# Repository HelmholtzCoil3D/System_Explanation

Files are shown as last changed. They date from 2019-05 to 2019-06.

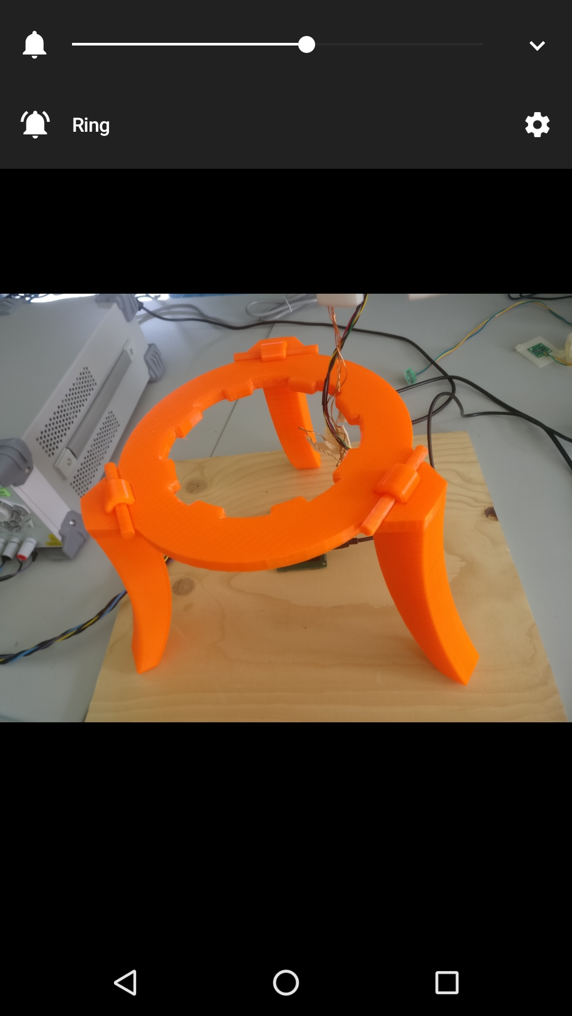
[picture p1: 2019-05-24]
Images/Print results/Screenshot_20190524-094820.jpg

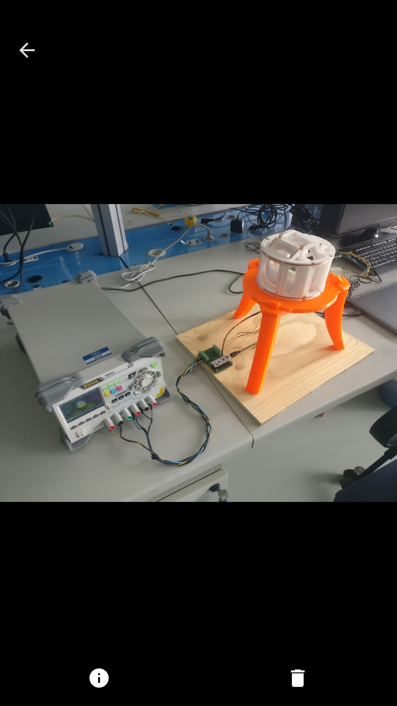
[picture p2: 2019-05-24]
Images/Final Results/Screenshot_20190524-155419.jpg

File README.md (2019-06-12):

# 3D Helmholtz coil system

This document explains how the system was made and how it works, with the purpose to make the reproduction of the project possible.

- [3D Helmholtz coil system](#3d-helmholtz-coil-system)
- [Objective of the project](#objective-of-the-project)
- [Base Knowledge](#base-knowledge)
- [Blocks diagram](#blocks-diagram)
- [Helmholtz coils design](#helmholtz-coils-design)
  - [Simulator](#simulator)
    - [Input parameters:](#input-parameters)
    - [Console results](#console-results)
    - [Graphical Results](#graphical-results)
    - [Simulator results](#simulator-results)
  - [3D models](#3d-models)
    - [3 axis helmholtz coil 3D model](#3-axis-helmholtz-coil-3d-model)
    - [Sensor and sample support 3D model](#sensor-and-sample-support-3d-model)
    - [Pegs 3D model](#pegs-3d-model)
    - [3 feet support 3D model](#3-feet-support-3d-model)
  - [3D Print results](#3d-print-results)
    - [Coils support print](#coils-support-print)
    - [Sensor/Sample support](#sensorsample-support)
    - [Pegs](#pegs)
  - [3 Feet support](#3-feet-support)
  - [Coils winding](#coils-winding)
  - [Practical results](#practical-results)
    - [Inner coil](#inner-coil)
    - [Middle coil](#middle-coil)
    - [External coil](#external-coil)
    - [Data analysis](#data-analysis)
- [Magnetic sensor](#magnetic-sensor)
- [Controller](#controller)
  - [Power Supply](#power-supply)
  - [H-bridges](#h-bridges)
  - [MCU](#mcu)
  - [New system Block Diagram](#new-system-block-diagram)
- [Integration](#integration)
  - [system_current_finder.py and system_measurement_procedure.py](#systemcurrentfinderpy-and-systemmeasurementprocedurepy)
  - [system_plot.py](#systemplotpy)
  - [system_realtime_field_adjusting.py](#systemrealtimefieldadjustingpy)
  - [System validation](#system-validation)
- [PCBs](#pcbs)
  - [Sensor PCB](#sensor-pcb)
  - [System PCB](#system-pcb)
- [Final result](#final-result)
- [System applications](#system-applications)

# Objective of the project

This project aim is to prototype some kind of system control it automaticaly and make some fields setups in static applications.

The idea behind this project is to create a homogeneous field in some defined region where magnetic samples can be tested with a totaly known field

<p align="center">
  
  
</p>

<p align="center">
  
</p>

The desired features in this case would be a region with errors bellow 1%, the maximium difference of the magnetic field strenght in two different points and angles with less than 1° of difference between two different points of the homogeneous region. A magnetic flux density range of 1 uT to 1 mT is desired in this region.

The region defined for the prototype at first is a **20 mm³**  region

**The system itself just generate the field**, the magnetic sample must have its own system to generate the data for posterior analysis. Analisys can be made based in the known direction and amplitude of the homogeneous region magnetic field.

# Base Knowledge

To create a homogeneous field in some free space region, the concept used was the [Helmholtz coil] that can create a homogeneous field inward from the coils to the geometric center of the estructure, the more in the center, the more homogeneous the field is.

Exitating the coils with a known current generates a known [magnetic field] (H) that is related to the magnetic flux density (B) by the permeability ($\mu$) of the material, in this case the air ([1.00000037])

The B can [saturate] depending on the material, in this case it will not happen so there are no linearity problems

Knowing that the magnetic field will be linear, so a 3 axis Helmholtz coil can be design to generate the arbitrary homogeneous magnetic field, remembering that this system must compensate the [earth magnetic field]

#  Blocks diagram

The system blocks diagram can be represented as follows:
<p align="center">
  
</p>

The main parts of the system:
-   Helmholtz coils to generate the field
-   Controller to control the generated field throught magnetic sensors readings and current supply for the coils
-   Interface to give properly the user commands to the controller

# Helmholtz coils design

## Simulator

To design the needed helmholtz coils, an open source python library was used, [magpylib], this library is capable to calculate magnetic field, through analytical solutions, of permanent magnets and current lines or current loops.

In fact the application is static, so the helmholtz can projected as current loops placed in a helmholtz coil shape.

<p align="center">
  
</p>

 From the cross-cut section the parameters for the coils calculation can be extracted as the following figure:

<p align="center">
  
</p>

The details about the calculator can be seen in the [Helmholtz coil calculator] and [Auxiliar library] files. Giving some parameters to the calculator, it gives us the necessary coil diameter to achieve the desired field in the center of the coil and graphics that shows the field strenght in the 3 vectors of the field separeted (x,y,z) and from this an analysis can be made to determine the homogenity of the field generated by each coil, amplitude and angle error relative to the center in the desired homogeneous region. Following the input and the results in this project.

### Input parameters:

Those are the input parameters for the calculator to find the diameter necessary the design each coil, following previous figure standards.

``` python
# have to use a little bit bigger value than wireExternalDiameter, if not, the wire will not fit inside
AllCoilsWireDiameter = (0.56 + 0.047)*1.09   # Wire diameter in mm (from dataSheet)

minRes = 0.06736                            # Ohms/m (from dataSheet)
nominal = 0.06940                           # Ohms/m (from dataSheet)
maxRes = 0.07153                            # Ohms/m (from dataSheet)

wireResistence = maxRes                     # Ohms/m (from dataSheet)

# z First Coil configuration

zInitialValueCoilDiameter = 80 # Initial value for the function that calculates the precise diameter

zCoilCurrent = 0.5             # Amperes
zLoopsInEachEvenLayer = 10     # The number of loops in each layer
zEvenLayers = 7                # The evenlayers always have to be equal to oddLayers or oddLayers + 1
zOddLayers = 7
zDesiredField = 1.25           # The desired field in the center of the Helmholtz coil

# y Second Coil configuration

yCoilCurrent = 0.5             # Amperes
yLoopsInEachEvenLayer = 6      # The number of loops in each layer
yEvenLayers = 3                # The evenlayers always have to be oddLayers + 1 or equal oddLayers
yOddLayers = 3
yDesiredField = 0.25           # The desired field in the center of the Helmholtz coil

# x Third Coil configuration

xCoilCurrent = 0.5             # Amperes
xLoopsInEachEvenLayer = 7      # The number of loops in each layer
xEvenLayers = 3                # The evenlayers always have to be oddLayers + 1 or equal oddLayers
xOddLayers = 3
xDesiredField = 0.25           # The desired field in the center of the Helmholtz coil
```

### Console results

Those are the results that shows up in the standard output, in this case the console of spyder, those results can estimate how much wire in meters and the power in watts that will be dissipated on each helmholtz coil individualy.



### Graphical Results

Those are the graphical results of the calculator. For each coil a graphic is generated with the amplitude of the magnetic field of a slice in the center of the coil, this slice must have the region of interest, it also displays a 3D graphic of what the system looks like. Those graphics can help to estimate the homogenity level of the whole region.

<p align="center">
  
  
</p>

<p align="center">
  
  
</p>

<p align="center">
  
  
</p>

As can be seen in the next figures, the calculator estimates the interference of the cables used to bring the current to the coils, the current passing throught them generates a field and it can be compared with the field generated for each coil. Just the field of the connectors is showed in the graphics. Another that can be seen is if the coils will be inside each other in the 3D representation, it's shown in the 3 coils figure that the coils don't touch each other in this case.

<p align="center">
  
  
</p>

<p align="center">
  
  
  
</p>

### Simulator results

After checking all the homogenity and interference stuff, the interested parameters to construct the coils support are shown in the next table:

Wire External Diameter = 0.6 mm

|Coils| Radius | Coil Width| Coil Height|
|:-:|-|-|-|
| Inner | 42.5 mm | 6.6 mm | 9.65 mm |
| Middle | 56.15 mm | 4 mm | 5.5 mm |
| External | 66.5 mm | 4.65 mm | 5.5 mm |
**\* rouded values**

## 3D models

With the high precision of the 3D printers ($\pm$ 1 $\mu$m) the idea was doing the 3 helmholtz coils all together in the same mechanical part, 1 piece. With this, the misalignment problems would desappear.

Misalignment example:
<p align="center">
  
</p>

To design the 3D model the utilized software was [solidWorks], a comercial software for 3D models design, good for geometric models. The design was made based in the simulating results. Besides the coils, the sensor and sample placement should be designed together with the coil, to make it easier to think the supports was separated and connected throught holes and pegs.

### 3 axis helmholtz coil 3D model

The 3 axis helmholtz coil 3D model design can be seen in the following images:

<p align="center">
  
  
  
</p>

It has some holes inside to attach the sensor support and a bigger hole in the middle for the cables to link the sensor to the system. In the bottom some support points to make the coil stable in the table.

### Sensor and sample support 3D model

After some tests, the model achieved for the PCB support is shown in the following image:

<p align="center">
  
  
</p>

This model perfectly fits inside the coils support model, using the internal part to support the sensor of the system and the more external pegs and holes to support the sample. Notice that the external support is designed in such a way that the sample stays in the middle of the coils. If the sample change, the user can design another 3D model for the support to adapt the coil usage to an especific application

### Pegs 3D model

To attach the PCB support to the coils support some pegs was designed with diferent diameters, using the fact that the printer has more precision than $\pm$1 $\mu$m:

<p align="center">
  
  
</p>

Using 50 $\mu$m of difference between the pegs, will make it safe to fit in the previous models holes, testing which diameter is beter to use.

### 3 feet support 3D model

To avoid some induction fields problems that could appear for some kind of measurements, a 3 feet support for the coils support was design that the coils support just fits inside of the 3 feet support and make some distance between the table metal supports and the coils.

<p align="center">
  
  
  
</p>

## 3D Print results

The company have its own 3D printers, one with really high resolutions for tiny parts and another with less resolution but with more space to print. The material is not so rigid in the high resolution printer and the prints have problems in the pos-printing process that causes some bendding problems, so for the coils support the print was made by [Reprap] Austria, that was more cheap and perfect printed than with the company printer. For the other models, the company printer was enought to do the job.

The Reprap Austria 3D printer size limit is **32**x**36**x**42** **cm**, been the largest coil external diameter around 15 cm, the printing size is fairly ok and if the company needs a bigger coil with different especification, it can be printed.

### Coils support print

The Coils support was ordered and the result can be seen:
<details>
<summary> <b>Click here to see the Coil support print result</b> </summary>
<p align="center">
  
</p>

**There's a sensor support inside of the coils printed with the company printer, that fitted really nice inside**
</details>

### Sensor/Sample support

Printed in the CTR high resolution printer:

<p align="center">
  
  
</p>

<p align="center">
  
  
</p>

### Pegs

Printed in the CTR high resolution printer:

<p align="center">
  
</p>

## 3 Feet support

Following figure shows the 3 feet suppport printed in the lower resolution printer, that is also very good and it's used for bigger 3D models.

<p align="center">
  
</p>

## Coils winding

After doing the windings really carefull, maintaining the [wire] stretched while doing each turn, it helped to get the wire really fit in the coils support. The arrangement to stretch the wire can be seen in the next image, its an improvised tool that makes some pressure in the reel, extremely important to make the coils the most near to the simulation position of the wires.

<p align="center">
  
  
</p>

 The [hot glue] was used to mantain the cables fixed in the coils suppor, the result of the 3 axis coil can be seen in the following image:

<p align="center">
  
  
</p>

Each of the six coils was done individualy, doing the inside coils first, and then connected with a solder point with the respective pair (2 coils in X direction to form the X helmholtz coil for example)

## Practical results

To validate the python calculator, some measurements was made, like the resistence, inductance and generated field for each coil. Each coil is named now by inner, middle and external coil. The measurements are discussed subsequently.

### Inner coil

This coil is the most inside coil (inner), it has the most intense field of the 3 coils, that's why it's the inside coil and the one that have more windings.

Coil teorethical features:
|Feature| Value |
|-|-|
|Current| 0 ~ 0.5 *A*|
|Magnetic field generated| 0 ~ 1.25 *mT* |
|MagField/Current ration| 2.5 |
|Coil resistence| 5.264 $\Omega$|

Mesured resistence ($\Omega$), inductance (mH):

<p align="center">
  
  
</p>

The mesured field with the 500 mA (powersupply and sensor image):

<p align="center">
  
  
</p>

### Middle coil

The middle coil is the one in between other 2 coils and its purpose is to cancel the earth magnetic field.

Coil teorethical features:
|Feature| Value |
|-|-|
|Current| 0 ~ 0.5 *A*|
|Magnetic field generated| 0 ~ 0.25 *mT* |
|MagField/Current ration| 0.5 |
|Coil resistence| 1.689 $\Omega$|

Mesured resistence, inductance:

<p align="center">
  
  
</p>

The mesured field with the 500 mA (powersupply and sensor image):

<p align="center">
  
  
</p>

### External coil

External coil is the name of the further coil from the center, the biggest, same purpose as middle coil.

Coil teorethical features:
|Feature| Value |
|-|-|
|Current| 0 ~ 0.5 *A*|
|Magnetic field generated| 0 ~ 0.25 *mT* |
|MagField/Current ration| 0.5 |
|Coil resistence| 2.356 $\Omega$|

Mesured resistence, inductance:

<p align="center">
  
  
</p>

The mesured field with the 500 mA (powersupply and sensor image):

<p align="center">
  
  
</p>

### Data analysis

In the previous images can be seen the current to excitate the coils and the magnetic field read from the sensor in **$\mu$T** (The sensor will be explained in the next topic), the magnetic field is already a mean of 30 measurements. The sensor can not be positioned perfectly aligned with the coils directions, then the norm of the difference should be taken to express the real value of the field generated by the coils. 

A python script ([Coil Features]) was made to handle those simple calculations and the results are shown in the next image.



As seen, the field error is really tiny (bellow 2%), maybe because the windings somehow are no perfectly round and it can be reflected in this tiny error.

In the resistance the error was quite big, but for an estimative could be helpfull to have some power dissipation notion.

# Magnetic sensor

The magnetic sensor is a really important part of the project, because it will provide the measurements to understand if the coils are working properly or not and the closes some loop to adjust the field if necessary. Some research was done and some sensors was tried. The first solution encounted was the [LIS3MDL] sensor, it's for compass application and had a good range of measurement for the application, but with some tests it showed really bad response to offset errors, so another one was tried, an upgraded version of this sensor from the same company ([ST]), [LSM303D], but somehow there was the same problems. Then researched for another companies that would be specialized in magnetic sensors and then found [MEMSIC], and searching for magnetic sensors, found one that fitted in the application, [MMC3416].

The sensor have I²C interface, also have a really interesting measurement procedure, where the [set/reset] operation can be applied to extract a better measurement, the downside of this procedure is that it takes time. In this project is not a problem because the application is static.



A usefull thing to do is buy the evaluation board in this case, that have everything in hardware set up to just use the sensor. To project, order and solder the PCB takes time, so to develop it faster the [MMC3416 evaluation board] was used.



# Controller

The controller part of the blocks diagram could be anything that could:

-   Control the coils field
-   Read the sensor measurements
-   Interpret the user commands

For those tasks more especificaly was needed something that could have some: 
-   I²C comunication (sensor) 
-   Current source adjustable with a good resolution, to achieve the field resolution bellow 1 uT
-   A way to change the current polarity in the coils
-   Kind of USB communication to stablish comunication with the computer (where the user interface would be implemented)

It's difficult to have all those tasks already integrated so some research was done to what to use.

## Power Supply

In one way or another, a power supply must be used to provide the energy for the coils, can be as a voltage source or a current source. Operating in the voltage source mode would imply some external controller to adjust the right current for the coils, in other way with the current source mode, the power supply must have some kind of electronic current control integrated to use this in the system. After some research found [Rigol DP800] series, specifically the 831A model, that have 0.1 mA resolution of current control with 3 channels and can be controlled by software, perfect for this application.

The software control can be done through the [python visa] that are some special libraries used to control mesurement equipaments.

[python visa]:https://pyvisa.readthedocs.io/en/latest/

<p align="center">
  
</p>

## H-bridges

To control the current polarity in the coils, a classical but really good solution can be used, the [H-bridge] control.

    

It's system composed by 2 switches, as shown in the first figure of this section. The circuit have 3 possible states, that are shown in the figures, one state is everything open (turn off), and the other two is the current flowing to one direction of the load and the other the current is flowing in the another direction.

A lot of research was done, and most of the integrated H bridges have underload protection what is not desirable for this project, but one was found with the potential to be used, the [DRV8838DSGR] IC.



This IC works with 2 digital pins to control the states and is based on N-Mosfets. It can operate in 0~11 V range which fit the application. The only downside is the fact that the load supply is not isolated from the control supply.

The power supply choosed for the current control has one of its channels a negative voltage source that is internaly connected to another positive channel. In this case the [DRV8838DSGR] H-bridge the internal connection in the references of the supply for the logic (Vcc) and the supply for the load (VM) would cause a short circuit between the negative voltage and the reference in the power supply.

For this specific channel, a different solution to also isolate the channel must be implemented. After some research the best solution would be use 4 relays to do the switch role controlling it in such a way to stay in the 3 possible states of the H-bridge. The component choosed for the switch was [CPC1002N], it's a solid-state relay, basicaly an optocoupler with more current capacity than a normal optocoupler.



## MCU

To control the H-bridges and the sensor a microcontroller can be used. The microcontroller must have:
-   I²C interface peripherical
-   At least 6 free digital pins (H bridges)
-   USB comunication peripherical

And for this the [STM32L4] was choosed because of the versatility, powerful processing, easy usage and low cost, And it has all the features necessary for the system.

[STM32L4]:https://www.st.com/resource/en/datasheet/stm32l432kc.pdf

To program this controller the [stm32CUBE] was used to generate the base code and the [atollic] to edit, compile, debug and program the code.

The main code developed for the microcontroller is in those files:

-   [main.c]
-   [main.h]
-   [lib_aux.c]
-   [lib_aux.h]
-   [MCC3416_def.h]

To have more robustness the system was developed in a [finite state machine] shape, with one state for each operation.

When the microcontroller starts-up the first thing that it does is asking throught USB comunication, the size of the mean for each measurement and the time (ms) to do it, of course the bigger the measurements number, bigger the overhead will be.

After the 2 responses, the system start to operate in the state machine where there are 9 possible states besides Iddle:

|State symbol| Description of the state|
|:-:|:-|
|'D'| Procedure mean size of measurements and return the mean in the USB comunication getting back to iddle after|
|'I'| Sets the polarity to 'set' in the H-bridge connected to the channel 2 and sends back "'I' done!"|
|'i'| Sets the polarity to 'reset' in the H-bridge connected to the channel 2 and sends back "'i' done!"|
|'M'| Sets the polarity to 'set' in the H-bridge connected to the channel 3 and sends back "'M' done!"|
|'m'| Sets the polarity to 'reset' in the H-bridge connected to the channel 3 and sends back "'m' done!"|
|'E'| Sets the polarity to 'set' in the H-bridge connected to the channel 1  and sends back "'E' done!"|
|'e'| Sets the polarity to 'reset' in the H-bridge connected to the channel 1 and sends back "'e' done!"|
|'S'| Set all the polarities to a reference and sends back "'S' done!"|
|'C'| Perform continuos measurement procedures and send then to the USB comunication without getting back to the IDDLE state|

<p align="center">
  
</p>

The 'I', 'i', 'E' and 'e' states control just the digital pin for the [DRV8838DSGR] H-bridge, the 'M' and 'm' states control 4 digital pins to control the H-bridge formed by the relays [CPC1002N].

After a state sending, the system response with a '"state" done!' for debug and flow control. The exception on this is the 'D' and 'C' states that respond with the data directly.

The USB comunication is based on UART, the baud rate of the comunication is 256000 bauds

## New system Block Diagram

With the definition of how the control will be done and with what, The blocks diagram can be redrawed into the following image:

<p align="center">
  
</p>

# Integration

With a research about how to integrate the VISA application and the USB data from microcontroller, the conclusion was to use python libraries to get the information from USB and to control the power supply, using a structered diferent scripts to do some procedure with this.

The main python libraries used for USB communication:
-   [pyvisa]
-   [pyserial]

for some data processing and to show graphics:
-   [numpy]
-   [matplotlib]

and used some standard libraries as:
-   [time]
-   [csv]
-   [re]

The existing scripts until now following:
-   [auxLib.py]
-   [system_current_finder.py]
-   [system_measurement_procedure.py]
-   [system_realtime_field_adjusting.py]
-   [spinning_Compass.py]
-   [system_plot.py]

auxLib is the library with the <s>Black Magic</s> functions that do all the work on the others scripts.

## system_current_finder.py and system_measurement_procedure.py

It calculates the necessary current to have a range of field from 'lowerFieldLimit' to 'upperFieldLimit' field, with a step of 'fieldResolution'. Running the system current finder script gives a `csv` file that contains the information to later apply it with the system measurement procedure file.

Something important to **take care** is that to calculate the currents, the coil must not move and must not have any magnetic object near to this, then in the measurement procedure, without moving the coil, just put the sample inside and apply the fields.

The calculated currents will be applied one at once, typing 'Enter' to go into the next calculated current.

## system_plot.py

Takes the `csv` file generated by [system_current_finder.py] and transform the information from text to graphics.

## system_realtime_field_adjusting.py

Set some field in the input code, 3 axis field, and then run the code. It will keep trying to adjust the field of the coils to reach the desired field inside the main region in closed-loop.

## System validation

After testing all the hardware, the scripts was developed 

**\* image of the system with the evaluation boards**

tiny Missing Image

Following the graphic generated by [system_plot.py] from a rotating x,y field found by [system_current_finder.py] for example:

<p align="center">
  
  
</p>

# PCBs

With the validated hardware, the next step would be doing a PCB to have a more reliable and less noisy system. The PCB's were ordered from [Eurocircuits Gmbh] using the PCB eagle files.

## Sensor PCB

To make things faster, a PCB for the sensor was made, but not attaching the sensor to it, because it's hard to solder it by hand, instead it was designed to attach the evaluation board to it using a SMD connector that clicks the cable to the PCB, reducing noise problems in the I²C communication.

[Eurocircuits Gmbh]:https://www.eurocircuits.com/

The schematic and layout:
<p align="center">
  
  
</p>

## System PCB
The results after soldered:
<p align="center">
  
  
</p>

The schematic and layout:
<p align="center">
  
  
</p>

The results after soldered:
<p align="center">
  
  
</p>

The cable with some twisted pairs for the noise reduction:
<p align="center">
  
</p>

The final result of the system:
<p align="center">
  
</p>

# Final result

[order list]

<p align="center">
  
  
</p>

<p align="center">
  
</p>

# System applications

**\* Using the [system_realtime_field_adjusting.py]**
<details>
<summary> <b>Click here to see the procedure to set the zero field</b> </summary>
<p align="center">
  
</p>

</details>
<details>
<summary> <b>Click here to see the compass in the zero field</b> </summary>
<p align="center">
  
</p>
</details>

</details>
<details>
<summary> <b>Click here to see the automatic measurements (fluxgate)</b> </summary>
<p align="center">

  System working

  

  Procedure flowChart

  

  Current finder results (-180 uT to 180 uT, 0.5 uT step)

  

  Data from osciloscope

  

  Data analysis

  
  

  result comparition (neosha work)
  
  

</p>
</details>

<details>
<summary> <b>Youtube videos</b> </summary>

[Compass zero field demonstration]

<iframe width="560" height="315" src="https://www.youtube.com/embed/eRR1c4607lU" frameborder="0" allow="accelerometer; autoplay; encrypted-media; gyroscope; picture-in-picture" allowfullscreen></iframe>

[Compass zero field procedure]
<iframe width="560" height="315" src="https://www.youtube.com/embed/aR3ZOZWw4vM" frameborder="0" allow="accelerometer; autoplay; encrypted-media; gyroscope; picture-in-picture" allowfullscreen></iframe>

[Automatic measurements]
<iframe width="560" height="315" src="https://www.youtube.com/embed/5FVGol-J0HI" frameborder="0" allow="accelerometer; autoplay; encrypted-media; gyroscope; picture-in-picture" allowfullscreen></iframe>

</details>

[Automatic measurements]:https://www.youtube.com/watch?v=5FVGol-J0HI

[order list]:ComponnentsListToOrder.md

[auxLib.py]:System_integration/auxLib.py

[system_current_finder.py]:System_integration/system_current_finder.py

[system_realtime_field_adjusting.py]:System_integration/system_realtime_field_adjusting.py

[system_measurement_procedure.py]:System_integration/system_measurement_procedure.py

[spinning_Compass.py]:System_integration/spinning_Compass.py

[system_plot.py]:System_integration/system_plot.py

[re]:https://docs.python.org/3/library/re.md?highlight=re#module-re
[csv]:https://docs.python.org/3/library/csv.md?highlight=csv#module-csv
[time]:https://docs.python.org/3/library/time.md
[matplotlib]:https://matplotlib.org/
[numpy]:https://www.numpy.org/
[pyvisa]:https://pyvisa.readthedocs.io/en/latest/
[pyserial]:https://pyserial.readthedocs.io/en/latest/pyserial.md

[MMC3416 evaluation board]:ttps://media.digikey.com/pdf/Data%20Sheets/MEMSIC%20PDFs/MMC3416PJ-B_UG.pdf

[set/reset]:http://www.seraphim.com.tw/upfiles/c_supports01284968029.pdf

[main.c]:Microcontroller/main.c

[main.h]:Microcontroller/main.h

[lib_aux.h]:Microcontroller/lib_aux.h

[lib_aux.c]:Microcontroller/lib_aux.c

[MCC3416_def.h]:Microcontroller/MCC3416_def.h

[CPC1002N]:http://www.ixysic.com/home/pdfs.nsf/www/CPC1002N.pdf/$file/CPC1002N.pdf

[DRV8838DSGR]:http://www.ti.com/lit/ds/symlink/drv8838.pdf

[H-bridge]:https://en.wikipedia.org/wiki/H_bridge

[Rigol DP800]:http://beyondmeasure.rigoltech.com/acton/attachment/1579/f-01c1/1/-/-/-/-/DP800%20Datasheet.pdf

[Compass zero field demonstration]:https://www.youtube.com/watch?v=eRR1c4607lU

[Compass zero field procedure]:https://www.youtube.com/watch?v=aR3ZOZWw4vM&t=

[Helmholtz coil calculator]:helmholtzCoilsSimulations/HelmholtzCoilCalculator.md

[Auxiliar library]:helmholtzCoilsSimulations/magpylibUtils.md

[Coil Features]:CoilFeatures.md

[magpylib]:https://github.com/magpylib/magpylib

[Helmholtz coil]:https://en.wikipedia.org/wiki/Helmholtz_coil

[magnetic field]:https://en.wikipedia.org/wiki/Magnetic_field

[earth magnetic field]:https://en.wikipedia.org/wiki/Earth%27s_magnetic_field

[1.00000037]:https://en.wikipedia.org/wiki/Permeability_(electromagnetism)

[saturate]:https://en.wikipedia.org/wiki/Saturation_(magnetic)

[coil img 1]:https://i.imgur.com/AkZzpYJ.jpg

[solidWorks]:https://www.solidworks.com/

[Reprap]:https://www.reprap.cc/

[hot glue]:https://en.wikipedia.org/wiki/Hot-melt_adhesive

[Missing Image]:https://i.imgur.com/0EmAI26.png

[wire]:https://at.rs-online.com/web/p/kupferdrahte/0357750/

[LSM303D]:https://www.pololu.com/file/0J703/LSM303D.pdf

[LIS3MDL]:https://www.st.com/resource/en/datasheet/lis3mdl.pdf

[MMC3416]:http://www.memsic.com/userfiles/files/Datasheets/Magnetic-Sensors-Datasheets/MMC3416xPJ_Rev_C_2013_10_30.pdf

[MEMSIC]:https://www.memsic.com/

[ST]:https://www.st.com/content/st_com/en.md

[Missing Image]:(https://i.imgur.com/0EmAI26.png)

[tiny Missing Image]:(https://i.imgur.com/zDgtWUj.png)

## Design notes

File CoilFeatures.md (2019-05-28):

```python
# -*- coding: utf-8 -*-

import numpy as np

theoreticalValue = [1250, 250, 250]

initialInner = [[12.75, 12.82, 12.88],[19.57, 19.55, 19.54],[48.76, 48.71, 48.74]]
initialMiddle = [[13.09, 12.77, 12.76],[19.76, 19.82, 19.80],[48.77, 48.76, 48.71]]
initialExternal = [[12.39, 12.40],[18.77, 18.79],[48.27, 48.34]]

finallInner = [[-1223.72, -1223.54, -1223.68],[16.45, 16.44, 16.44],[48.69, 48.68, 48.74]]
finalMiddle = [[7.86, 7.82, 7.82],[-230.55, -230.53, -230.47],[50.31, 50.33, 50.29]]
finalExternal = [[11.32, 11.57, 11.51],[15.59, 15.45, 15.43],[-205.35,-205.28,-205.38 ]]

for i in range(0,3):
    initialInner[i] = np.mean(initialInner[i])
    initialMiddle[i] = np.mean(initialMiddle[i])
    initialExternal[i] = np.mean(initialMiddle[i])

for i in range(0,3):
    finallInner[i] = np.mean(finallInner[i])
    finalMiddle[i] = np.mean(finalMiddle[i])
    finalExternal[i] = np.mean(finalExternal[i])
    
fieldInner = [0,0,0]
fieldMiddle = [0,0,0]
fieldExternal = [0,0,0]

for i in range(0,3):
    fieldInner[i] = finallInner[i] - initialInner[i]
    fieldMiddle[i] = finalMiddle[i] - initialMiddle[i]
    fieldExternal[i] = finalExternal[i] - initialExternal[i]

print('Field on inner coil with 500 mA')
print(fieldInner)

print('\nField on middle coil with 500 mA')
print(fieldMiddle)

print('\nField on external coil with 500 mA')
print(fieldExternal)

print('\nNorm of the fields:')
print(np.linalg.norm(fieldInner))
print(np.linalg.norm(fieldMiddle))
print(np.linalg.norm(fieldExternal))

print('\nError from theoretical values')
print(str((np.linalg.norm(fieldInner) - theoreticalValue[0])/theoreticalValue[0]*100) + ' %')
print(str((np.linalg.norm(fieldMiddle) - theoreticalValue[1])/theoreticalValue[1]*100) + ' %')
print(str((np.linalg.norm(fieldExternal) - theoreticalValue[2])/theoreticalValue[2]*100) + ' %')

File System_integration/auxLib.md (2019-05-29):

```python
# -*- coding: utf-8 -*-
"""
Auxiliar library for the Serial and User interface for the Helmholtz 3Dcoil project

Tarcis Becher
CTR
"""

#%% Imports ---------------------------------------------------------------------------------------------------------

import os
import numpy as np
import re
import datetime
import visa
import serial
import serial.tools.list_ports
from time import sleep

# -------------------------------------------------------------------------------------------------------------------
#%% Definitions -----------------------------------------------------------------------------------------------------

MCUcomText = 'STMicroelectronics STLink Virtual COM Port'
csvFileDir = "./csvData/"
regexSampleFinder = "(-?\w*.\w*);"

# -------------------------------------------------------------------------------------------------------------------
#%% Auxiliar function -----------------------------------------------------------------------------------------------
class CurrentCalculatorObj():
      
    def __init__(self, channel, zeroField, uT_to_mA, mA_to_uT, infCurrentLim = 0.1, supCurrentLim = 500):
        
        self.channel = channel
        self.infCurrentLim = infCurrentLim # mA
        self.supCurrentLim = supCurrentLim # mA
        self.zeroField = zeroField
        self.uT_to_mA = uT_to_mA
        self.mA_to_uT = mA_to_uT
        
        if self.zeroField > 0:
            self.zeroFieldSense = 1
        else:
            self.zeroFieldSense = -1
            
        self.incrementSense = 1

    def calculateCurrent(self, Field):
        if Field >= self.zeroField:
            self.incrementSense = 1
        else :
            self.incrementSense = -1
        
        current = (self.zeroField*self.zeroFieldSense + Field*self.incrementSense)*self.uT_to_mA
        
        if self.zeroField > 0:
            current = -current
            
        #print(current)
        
        return current

    # sets'n gets
    def set_uT_to_mA(self, new_uT_to_mA):
        self.uT_to_mA = new_uT_to_mA
        
    def get_uT_to_mA(self):
        return self.uT_to_mA
    
    def set_mA_to_uT(self, new_mA_to_uT):
        self.mA_to_uT = new_mA_to_uT
        
    def get_mA_to_uT(self):
        return self.mA_to_uT
    
    def setSupCurrentLim(self, newsupCurrentLim):
        self.supCurrentLim = newsupCurrentLim
        
    def getSupCurrentLim(self):
        return self.supCurrentLim
    
    def setInfCurrentLim(self, newinfCurrentLim):
        self.infCurrentLim = newinfCurrentLim
        
    def getInfCurrentLim(self):
        return self.infCurrentLim
    
    def setZeroFieldSense(self, newzeroFieldSense):
        self.zeroFieldSense = newzeroFieldSense
        
    def getZeroFieldSense(self):
        return self.zeroFieldSense
    
    def setSentidoDeIncremento(self, newSentidoDeIncremento):
        self.incrementSense = newSentidoDeIncremento
        
    def getSentidoDeIncremento(self):
        return self.incrementSense

    def setZeroField(self, newZeroField):
        self.zeroField = newZeroField
        
    def getZeroField(self):
        return self.zeroField
    
    def setChannel(self, newChannel):
        self.channel = newChannel
        
    def getChannel(self):
        return self.channel

class storeDataObj:
    def __init__(self, rotationMatrix):
        self.current = list()
        self.field = [list(),list(),list()]
        self.channel = list()
        self.rotationMatrix = rotationMatrix
        self.zeroField = list()
        self.control = list()
        self.index = 0
        
    def storeData(self, field, current, channel, zeroField, control):
        self.field[0].append(field[0])
        self.field[1].append(field[1])
        self.field[2].append(field[2])
        self.current.append(current)
        self.channel.append(channel)
        self.zeroField.append(zeroField)
        self.control.append(control)
        self.index += 1
    
    def createCSVfile(self, fileDir, fileName):
        #date = WhatTimeIsIt()
        #fileName = date[0:10] + "-" + date[11:13] + "-" + date[14:16] + "-" + date[17:19]
        #fileName = 'tests'
        makeDir(fileDir)
        fileCsv = createAndOpenFile(fileDir, fileName, ".csv")
        fileCsv.write("RotationMatrix;" + 
                      str(self.rotationMatrix[0][0]) + ";" + 
                      str(self.rotationMatrix[0][1]) + ";" + 
                      str(self.rotationMatrix[0][2]) + ";" + 
                      str(self.rotationMatrix[1][0]) + ";" + 
                      str(self.rotationMatrix[1][1]) + ";" + 
                      str(self.rotationMatrix[1][2]) + ";" + 
                      str(self.rotationMatrix[2][0]) + ";" + 
                      str(self.rotationMatrix[2][1]) + ";" + 
                      str(self.rotationMatrix[2][2]) + ";" + "\n")
        fileCsv.write("Axis X; Axis Y; Axis Z; Current; Channel; Date \n")
        i = 0
        #print('what')
        while (i <  len(self.current)):
            self.index -= 1
            data = [str(float(self.field[0][i])), str(float(self.field[1][i])), str(float(self.field[2][i])), 
                    str(float(self.current[i])), str(float(self.channel[i])), str(float(self.zeroField[i])), self.control[i]]
            #print(i)
            i += 1
            try:
                j = 0
                while (j < len(data)):
                    fileCsv.write(data[j])
                    fileCsv.write(";")
                    j+=1     
                fileCsv.write(WhatTimeIsIt())
                fileCsv.write("\n")
            except Exception as error:
                print(error)
            
        closeFile(fileCsv)
   
def closedLoopAdjust(visaObj, serialObj, channel, samplingTime, desiredField, rotationMatrix, initialValue, supLim, control = 'Current', breakCondition = 0.5, maxIterations = 20):
    
    iAnt = initialValue
    eAnt = 0
    index = 0

    while (1):
        
        i = eAnt*samplingTime + iAnt        
        
        if i > supLim:
            i = supLim
        if i < -supLim:
            i = -supLim
            
        if i >= 0:
            if channel == 1:
                changeCoilPolarity(serialObj, 'resetExternal')
            elif channel == 2:
                changeCoilPolarity(serialObj, 'resetInner')
            elif channel == 3:
                changeCoilPolarity(serialObj, 'resetMiddle')
        else:
            if channel == 1:
                changeCoilPolarity(serialObj, 'setExternal')
            elif channel == 2:
                changeCoilPolarity(serialObj, 'setInner')
            elif channel == 3:
                changeCoilPolarity(serialObj, 'setMiddle')
        if control == 'Current':
            setPowerSupplyChCurrent(visaObj, channel, float(i/1000)) 
        else:
            setPowerSupplyChVoltage(visaObj, channel, float(i/1000)) 
        
        #print('vish')
        fData = getMeasurement(serialObj)
        newField = np.matmul(rotationMatrix, fData)
        #print(newField)
        e = desiredField - newField[channel-1]
        #print(e)
        eAnt = e
        iAnt = i
        
        index += 1
        if (np.linalg.norm(e) < breakCondition):
            break
        if index > maxIterations:
            break    
        
    return newField, i, e

def setField(visaObj, serialObj, CurrentCalculatorObjObj, samplingTime, desiredField, rotationMatrix, breakCondition = 0.3, maxIterations = 20):
        
    current = CurrentCalculatorObjObj.calculateCurrent(desiredField)
    
    #infLim = CurrentCalculatorObjObj.getInfCurrentLim()
    supLim = CurrentCalculatorObjObj.getSupCurrentLim()
    #errorMessage = print("Current transpassed the limit, it's ajusted to de limit")
        
    channel = CurrentCalculatorObjObj.getChannel()
    
    voltFlag = 0
    if current < 0.1:
        if current > 0:
            voltFlag = 1
    if current > -0.1:
        if current < 0:
            voltFlag = 1
    
    if voltFlag :
        
        control = 'Voltage'
        setPowerSupplyChCurrent(visaObj, channel, float(supLim/1000)) 
        setPowerSupplyChVoltage(visaObj, channel, 0)
        
    else:
        control = 'Current'    
        setPowerSupplyChCurrent(visaObj, channel, float(current/1000)) 
        setPowerSupplyChVoltage(visaObj, channel, 4)
    
    if current >= 0:
        if channel == 1:
            changeCoilPolarity(serialObj, 'resetExternal')
        elif channel == 2:
            changeCoilPolarity(serialObj, 'resetInner')
        elif channel == 3:
            changeCoilPolarity(serialObj, 'resetMiddle')
    else:
        if channel == 1:
            changeCoilPolarity(serialObj, 'setExternal')
        elif channel == 2:
            changeCoilPolarity(serialObj, 'setInner')
        elif channel == 3:
            changeCoilPolarity(serialObj, 'setMiddle')
        #current = -current
           
    if control == 'Current':
        # closed loop control code     
        initialValue = current
    else:
        initialValue = 0
    
    newField, i, er = closedLoopAdjust(visaObj, serialObj, channel, samplingTime, desiredField, rotationMatrix, initialValue, supLim, control = control, breakCondition = breakCondition, maxIterations = maxIterations)
    
    #print(er)
        
    return newField, i, control 

def updateCoilPolarity(serialObj, current, channel):
    
    if current >= 0:
        if channel == 1:
            changeCoilPolarity(serialObj, 'resetExternal')
        elif channel == 2:
            changeCoilPolarity(serialObj, 'resetInner')
        elif channel == 3:
            changeCoilPolarity(serialObj, 'resetMiddle')
    else:
        
        if channel == 1:
            changeCoilPolarity(serialObj, 'setExternal')
        elif channel == 2:
            changeCoilPolarity(serialObj, 'setInner')
        elif channel == 3:
            changeCoilPolarity(serialObj, 'setMiddle')

def getDataFromReader(reader, dataOffset, rotationMatrixFlag = True):
    index = 0
    zeroField = np.zeros((3,1))
    channel = list()
    floatData = [list(), list(), list(), list()]
    rotationMatrixMeasures = np.zeros((3,3))
    control = list()
    j = 0
    for row in reader:
        flag0 = 1
        flag1 = 1
        flag2 = 1
        
        if rotationMatrixFlag:
            if index == 0:
                fData = strToFloat(row[1:10])
                rotationMatrixMeasures[0][0] = fData[0]
                rotationMatrixMeasures[0][1] = fData[1]
                rotationMatrixMeasures[0][2] = fData[2]
                rotationMatrixMeasures[1][0] = fData[3]
                rotationMatrixMeasures[1][1] = fData[4]
                rotationMatrixMeasures[1][2] = fData[5]
                rotationMatrixMeasures[2][0] = fData[6]
                rotationMatrixMeasures[2][1] = fData[7]
                rotationMatrixMeasures[2][2] = fData[8]
        if index > dataOffset:
            fData = strToFloat(row[0:5])
            floatData[0].append(fData[0])
            floatData[1].append(fData[1])
            floatData[2].append(fData[2])
            floatData[3].append(fData[3])
            channel.append(int(fData[4]))
            control.append(row[6:7])
            if j < 3:
                if fData[4] == 3:
                    if (flag0):
                        zeroField[2] = strToFloat(row[5:6])
                        j += 1
                        flag0 = 0
                if fData[4] == 2:
                    if (flag1):
                        zeroField[1] = strToFloat(row[5:6])
                        j += 1
                        flag1 = 0
                if fData[4] == 1:
                    if (flag2):
                        zeroField[0] = strToFloat(row[5:6])
                        j += 1
                        flag2 = 0
        index += 1
    return floatData, channel, zeroField, rotationMatrixMeasures, control

def rotationMatrixCalculator(visaObj, serialObj, teorethicalValue):
    
    # Rotation matrix, to align the measurements with the Coils axis
    fData = getMeasurement(serialObj)    
    # print(fData)
    
    # buffer to do the rotation matrix measurements
    bufferData = np.zeros((4,3))
    
    # Assuming that the measurement is precise enough
    bufferData[0,0] = fData[0]
    bufferData[0,1] = fData[1]
    bufferData[0,2] = fData[2]
    
    # Setting the voltage for the power supply
    setPowerSupplyAllChVoltage(visaObj, 4)
    
    # Current used in the coils to make the relationship between current and field measured
    baseCurrent = 400 #mA
    
    # Code to get the measurement information for the rotation matrix
    for i in range(3,0,-1):
        
        setPowerSupplyChCurrent(visaObj, i, baseCurrent/1000)
        sleep(0.1)
        
        fData = getMeasurement(serialObj)
        
        setPowerSupplyChCurrent(visaObj, i, 0)
        sleep(0.1)    
        
        bufferData[i,0] = fData[0] - bufferData[0,0]
        bufferData[i,1] = fData[1] - bufferData[0,1]
        bufferData[i,2] = fData[2] - bufferData[0,2]
        
    # Doing a linear relationship between the Current set in the coil and the Field measured with this 
    ch1Field = np.linalg.norm(bufferData[1,:])
    ch1Current = baseCurrent
    
    ch2Field = np.linalg.norm(bufferData[2,:])
    ch2Current = baseCurrent
    
    ch3Field = np.linalg.norm(bufferData[3,:])
    ch3Current = baseCurrent

    CurrentToField = np.zeros((3,1))
    FieldToCurrent = np.zeros((3,1))
    
    # Linear coeficients to converto from uT to mA and vice-versa
    CurrentToField[0] = ch1Field/ch1Current
    FieldToCurrent[0] = 1/CurrentToField[0]
    
    CurrentToField[1] = ch2Field/ch2Current
    FieldToCurrent[1] = 1/CurrentToField[1]
    
    CurrentToField[2] = ch3Field/ch3Current
    FieldToCurrent[2] = 1/CurrentToField[2]
    
    relationshipError = np.zeros((3,1))
    
    relationshipError[0] = np.linalg.norm(CurrentToField[0] - teorethicalValue[0])/teorethicalValue[0]*100
    relationshipError[1] = np.linalg.norm(CurrentToField[1] - teorethicalValue[1])/teorethicalValue[1]*100
    relationshipError[2] = np.linalg.norm(CurrentToField[2] - teorethicalValue[2])/teorethicalValue[2]*100
    
    #print("field/current ration error (%) for each coil")
    #print(relationshipError)
    
    # Those are the equations used to find the coeficients for the rotation matrix
    '''
    Ix0 = Cx1*xM0 + Cx2*yM0 + Cx3*zM0
    Ix1 = Cx1*xM1 + Cx2*yM1 + Cx3*zM1
    Ix2 = Cx1*xM2 + Cx2*yM2 + Cx3*zM2
    
    Iy0 = Cy1*xM0 + Cy2*yM0 + Cy3*zM0
    Iy1 = Cy1*xM1 + Cy2*yM1 + Cy3*zM1
    Iy2 = Cy1*xM2 + Cy2*yM2 + Cy3*zM2
    
    Iz0 = Cz1*xM0 + Cz2*yM0 + Cz3*zM0
    Iz1 = Cz1*xM1 + Cz2*yM1 + Cz3*zM1
    Iz2 = Cz1*xM2 + Cz2*yM2 + Cz3*zM2
    '''
    
    # The code to arrange the equations to get the rotation coeficients
    I1 = np.array([baseCurrent,0,0])
    I2 = np.array([0,baseCurrent,0])
    I3 = np.array([0,0,baseCurrent])
    M = np.zeros((3,3))
    
    for i in range(1,4):
        for j in range(0,3):
            M[i-1,j] = bufferData[i,j]
    
    # Solving the 3x3 systems
    C1 = np.linalg.solve(M,I1)*ch1Field/ch1Current
    C2 = np.linalg.solve(M,I2)*ch2Field/ch2Current
    C3 = np.linalg.solve(M,I3)*ch3Field/ch3Current
    
    # The rotation matrix 'C' that transform the uT measurement raw to the coils direction measurement in uT too
    rotationMatrix = [C1, C2, C3]
    
    # Reseting the Power Supply
    setPowerSupplyAllChCurrent(visaObj, 0)
    setPowerSupplyAllChVoltage(visaObj, 4)
    
    sleep(0.1)
    
    return rotationMatrix, CurrentToField, FieldToCurrent, relationshipError

def COMdetect(COMdescription = MCUcomText, errorMessage = 'MCU COM not detected'):
    xablau = serial.tools.list_ports.comports()
    for i in range(0,len(xablau)):
        #print(xablau[i],[1])
        ue = xablau[i][1].find(COMdescription)
        if ue != -1:
            COM = xablau[i][0]
            break
        else:
            COM = errorMessage
    return COM

def waitForNewData(serial, nTries = 10, tryTime = 0.001):
    
    i = 0
    while 1:
        if serial.in_waiting > 5:
            return 0
        else:
            sleep(tryTime)
            i += 1
        if i > nTries:
            #print('dataWaiting tries overflow')
            return 1

def getDataFromSerial(serial, regexSampleFinder):
    strXYZSamples = re.findall(regexSampleFinder, str(serial.readline()))
    #print(strXYZSamples)
    serial.reset_input_buffer()
    return strXYZSamples

def createSerialObj(COM, baudrate = 256000):
    return serial.Serial(COM, timeout=0.5, baudrate = baudrate)

def getDataFromSerialToString(serial, regexSampleFinder, time_ms):
    
    try:
        waitForNewData(serial,tryTime = float(time_ms)/1000)
            
        return getDataFromSerial(serial, regexSampleFinder)   
    
    except Exception as error:
        print(error)
        return 0

def strToFloat(strData):
    i = 0
    floatData = np.ones((len(strData),1), float, 'C')
    while (i < len(strData)):
        floatData[i] = float(strData[i])
        i += 1
    return floatData

def WhatTimeIsIt():
    justTime = str(datetime.datetime.now())
    return justTime[0:22]

def writeDataOnFile(file, data = [0]):
    
    try:
        i = 0
        while (i < len(data)):
            file.write(data[i])
            file.write(";")
            i+=1     
        file.write(WhatTimeIsIt())
        file.write("\n")
        return 0
    except Exception as error:
        print(error)
        return -1

def makeDir(director):
    
    try:
        os.makedirs(director)
    except FileExistsError:
        # directory already exists
        pass

def createAndOpenFile(folder, name, ext):
    
    filePath = folder + name + ext
    
    return open(filePath,"w+")
    
def closeSerialObj(serial):
    serial.close()
    
def closeFile(file):
    file.close()
    
def sendCommandPS(instrument , command):
    instrument.write(command)  
    sleep(0.01)

def startupCoilsPolarity(serialObj):
    i = 0;
    serialObj.reset_input_buffer()
    serialObj.reset_output_buffer()
    while 1:
        serialObj.write(b'S')
        #print(i)
        i+=1
        if 0 == waitForNewData(serialObj):
            check = str(serialObj.readline())
            #print(check)
            serialObj.reset_input_buffer()
            if check == "b'S Done\\n'":
                break
        else:
            if i > 10:
                serialObj.reset_input_buffer()
                break

def changeCoilPolarity(serialObj, Coil):
    i = 0;
    serialObj.reset_input_buffer()
    serialObj.reset_output_buffer()
    while 1:
        if Coil == 'setExternal':
            serialObj.write(b'E')
        elif Coil == 'resetExternal':
            serialObj.write(b'e')
        elif Coil == 'setMiddle':
            serialObj.write(b'M')
        elif Coil == 'resetMiddle':
            serialObj.write(b'm')
        elif Coil == 'setInner':
            serialObj.write(b'I')
        elif Coil == 'resetInner':
            serialObj.write(b'i')
        else:
            raise Exception("This Coil reference doesn't exist")
            
        i+=1
        if 0 == waitForNewData(serialObj):
            check = str(serialObj.readline())
            #print(check)
            serialObj.reset_input_buffer()
            if check == "b'E Done\\n'":
                break
            if check == "b'I Done\\n'":
                break
            if check == "b'M Done\\n'":
                break
            if check == "b'e Done\\n'":
                break
            if check == "b'i Done\\n'":
                break
            if check == "b'm Done\\n'":
                break
        else:
            if i > 200:
                serialObj.reset_input_buffer()
                break
            
def inChangeCoilPolarity(serialObj):
    i = 0;
    serialObj.reset_input_buffer()
    serialObj.reset_output_buffer()
    while 1:
        serialObj.write(b'I')
        i+=1
        if 0 == waitForNewData(serialObj):
            serialObj.reset_input_buffer()
            break
        else:
            if i > 10:
                serialObj.reset_input_buffer()
                break

def midChangeCoilPolarity(serialObj):
    i = 0;
    serialObj.reset_input_buffer()
    serialObj.reset_output_buffer()
    while 1:
        serialObj.write(b'M')
        i+=1
        if 0 == waitForNewData(serialObj):
            serialObj.reset_input_buffer()
            break
        else:
            if i > 10:
                serialObj.reset_input_buffer()
                break
    
def exChangeCoilPolarity(serialObj):   
    i = 0;
    serialObj.reset_input_buffer()
    serialObj.reset_output_buffer()
    while 1:
        serialObj.write(b'E')
        i+=1
        if 0 == waitForNewData(serialObj):
            serialObj.reset_input_buffer()
            break
        else:
            if i > 10:
                serialObj.reset_input_buffer()
                break

def getMeasurement(serialObj):
    i = 0;
    serialObj.reset_input_buffer()
    while 1:
        fData = [0,0,0]
        serialObj.write(b'D')
        i+=1
        if 0 == waitForNewData(serialObj):   
            strData = getDataFromSerial(serialObj, regexSampleFinder)
            if i == 8:
                return fData
            if len(strData) == 3:
                fData = strToFloat(strData)
            else:  
                print(strData)
                serialObj.reset_input_buffer()
                if i == 5:
                    return fData
                continue
            serialObj.reset_input_buffer()
            return fData

def startUpPowerSupply(resource_name = 'USB0::0x1AB1::0x0E11::DP8A203800261::0::INSTR'):
    
    rm = visa.ResourceManager() # To connect the wraper to the USB driver
    dp800 = rm.open_resource(resource_name) # Open a resource that can comunicate with RIGOL PS
    # setup to starts the procedure
    dp800.write("SOUR1:VOLT 0")
    dp800.write("SOUR1:CURR 0")  
    sleep(0.1)
    dp800.write("SOUR2:VOLT 0")
    dp800.write("SOUR2:CURR 0")
    sleep(0.1)
    dp800.write("SOUR3:VOLT 0")
    dp800.write("SOUR3:CURR 0")
    sleep(0.1)
    
    dp800.write('OUTP CH1,ON')  # Enabling the Channel 1 output
    dp800.write('OUTP CH2,ON')  # Enabling the Channel 1 output
    dp800.write('OUTP CH3,ON')  # Enabling the Channel 1 output
    
    return rm, dp800
    
def closingPowerSupplyChannel(dp800, rm):
    dp800.close()
    rm.close()
    
def setupMCU(serialObj, samplesPerMean, timeBetweenSamples):
    sleep(0.1)
    serialObj.write(samplesPerMean)
    sleep(0.1)
    serialObj.write(timeBetweenSamples)
    serialObj.reset_input_buffer()
    sleep(0.1)
    
def setPowerSupplyAllChCurrent(visaObj, Current):
    sendCommandPS(visaObj, 'SOUR1:CURR '+str(Current))
    sendCommandPS(visaObj, 'SOUR2:CURR '+str(Current))
    sendCommandPS(visaObj, 'SOUR3:CURR '+str(Current))
    
def setPowerSupplyAllChVoltage(visaObj, Voltage):
    sendCommandPS(visaObj, 'SOUR1:VOLT '+str(Voltage))
    sendCommandPS(visaObj, 'SOUR2:VOLT '+str(Voltage))
    sendCommandPS(visaObj, 'SOUR3:VOLT '+str(-Voltage))

def setPowerSupplyChVoltage(visaObj, Channel, Voltage):
    sendCommandPS(visaObj, 'SOUR'+str(Channel)+':VOLT '+str(Voltage))
    
def setPowerSupplyChCurrent(visaObj, Channel, Current, security = True):
    if security:
        if Current > 0.5:
            Current = 0.5
    sendCommandPS(visaObj, 'SOUR'+str(Channel)+':CURR '+str(Current))
    
# -------------------------------------------------------------------------------------------------------------------

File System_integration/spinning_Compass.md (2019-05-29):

```python
# -*- coding: utf-8 -*-
"""
Created on Thu May 16 13:18:26 2019

@author: CTR Magnetic Demo
"""

# -*- coding: utf-8 -*-
"""
Created on Mon May 13 13:02:43 2019

@author: CTR Magnetic Demo
"""

#%% Imports

import numpy as np
import csv
from time import sleep
from auxLib import  updateCoilPolarity, getDataFromReader, rotationMatrixCalculator, strToFloat, storeDataObj, writeDataOnFile, CurrentCalculatorObj, setField, startupCoilsPolarity, closeFile, closeSerialObj, createAndOpenFile, WhatTimeIsIt, makeDir, createSerialObj, COMdetect, changeCoilPolarity, measurementNtransformation, setPowerSupplyChVoltage, setPowerSupplyAllChVoltage, setPowerSupplyAllChCurrent, setupMCU, closingPowerSupplyChannel, startUpPowerSupply, getMeasurement, setPowerSupplyChCurrent

#%% User code

samplesPerMean = b'2'
timeBetweenSamples = b'100'
measurementPeriod = 0.00

csvPath = "./csvData/"
csvFileName = "fieldsNcurrents2"

#%%

# To show numbers in console in the raw representation
np.set_printoptions(suppress=True)

fileField = csvPath + csvFileName + ".csv"

file = open(fileField, 'r')
reader = csv.reader(file, delimiter=';', quoting=csv.QUOTE_NONE)
floatData, channel, zeroField, rotationMatrixMeasures, control = getDataFromReader(reader, 1)
file.close()

#%% Start up code    
#closeSerialObj(serialObj)
# Teorethical values for field/current ration
teorethicalRelationship = [0.5, 2.5, 0.5]

try:
    # opening MCU comunication
    COM = COMdetect()
    
    serialObj = createSerialObj(COM)
        
    # Opening the MCU comunication channel
    setupMCU(serialObj, samplesPerMean, timeBetweenSamples)
    sleep(0.1)
    startupCoilsPolarity(serialObj)
    
    resource_name = 'USB0::0x1AB1::0x0E11::DP8A203800261::0::INSTR'       
    rm, dp800 = startUpPowerSupply(resource_name)
    
    rotationMatrix = rotationMatrixMeasures
       
    # comparing the zero fields
    setPowerSupplyAllChVoltage(dp800, 4)
    setPowerSupplyAllChCurrent(dp800, 0)
    
    fData = getMeasurement(serialObj)
    zeroFieldMeasured = np.matmul(rotationMatrix, fData)
    
    error = np.zeros((3,1))
    for i in range(0,3):
        error [i]= (zeroFieldMeasured[i] - zeroField[i])
    print("zero field absolute diference:")
    print(error)
    
    currentOffset = [0,0,0]
    
    for i in range(0,3):
        currentOffset[i] = 0#error[i]/teorethicalRelationship[i]    
            
    currents = floatData[3]
    newMeasures = np.zeros((len(currents),3))
    errors= np.zeros((len(currents),3))
    dp800.write("DISP:MODE NORM")
    sleep(0.01)
    i = 0
    indexSum = 1
    xablau = 240
    flag = 1
    time = 2
    a = 0
    b = 0
    for j in range(0,3):
        updateCoilPolarity(serialObj, currents[j], channel[j])
        dp800.write('SOUR'+str(int(channel[j]))+':CURR '+str(float(currents[j]/1000)))
    
    while(1):
        
        xablau2 = xablau + currents[1]
        dp800.write('SOUR'+str(int(2))+':CURR '+str(float(xablau2/1000)))
        dp800.write('SOUR'+str(int(3))+':CURR '+str(float(0/1000)))
        updateCoilPolarity(serialObj, xablau2, 2)
        sleep(time)
        
        xablau3 = xablau + currents[0]
        dp800.write('SOUR'+str(int(3))+':CURR '+str(float(xablau3/1000)))
        dp800.write('SOUR'+str(int(2))+':CURR '+str(float(0/1000)))
        updateCoilPolarity(serialObj, xablau3, 3)
        sleep(time)
        
        xablau2 = -xablau + currents[1]
        dp800.write('SOUR'+str(int(2))+':CURR '+str(float(xablau2/1000)))
        dp800.write('SOUR'+str(int(3))+':CURR '+str(float(0/1000)))
        updateCoilPolarity(serialObj, xablau2, 2)
        sleep(time)
        
        xablau3 = -xablau + currents[0]
        dp800.write('SOUR'+str(int(3))+':CURR '+str(float(xablau3/1000)))
        dp800.write('SOUR'+str(int(2))+':CURR '+str(float(0/1000)))
        updateCoilPolarity(serialObj, xablau3, 3)
        sleep(time)
        
        b = a
        a = WhatTimeIsIt()
        a = float(a[18:23])
        print(a-b)
    
    closeSerialObj(serialObj)
    closingPowerSupplyChannel(dp800, rm)
    
except Exception as error:

    print(error)
    
    closeSerialObj(serialObj)
    closingPowerSupplyChannel(dp800, rm)

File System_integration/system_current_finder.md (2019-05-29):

```python# -*- coding: utf-8 -*-
"""
py file that automatic sets the field of the 3DHC
"""
#%% Imports

import numpy as np
from time import sleep
import csv
from auxLib import  rotationMatrixCalculator, storeDataObj, writeDataOnFile, CurrentCalculatorObj, setField, startupCoilsPolarity, closeFile, closeSerialObj, createAndOpenFile, WhatTimeIsIt, makeDir, createSerialObj, COMdetect, changeCoilPolarity, measurementNtransformation, setPowerSupplyChVoltage, setPowerSupplyAllChVoltage, setPowerSupplyAllChCurrent, setupMCU, closingPowerSupplyChannel, startUpPowerSupply, getMeasurement, setPowerSupplyChCurrent

# To show numbers in console in the raw representation
np.set_printoptions(suppress=True)
#%% Channel controller class
#closeSerialObj(serialObj)

try:
#if 1:
    #%% User code
    # Setup information to the microcontroller, must be in binary format "b'information'"
    samplesPerMean = b'2'
    timeBetweenSamples = b'100'
    samplingTime = 0.1
    gain = 5
    
    fileDir = "./csvData/"
    fileName = 'fieldsNcurrents2'
    
    # Magnetic field in uT
    #pattern = 'straight'
    pattern = 'Circular'
    lowerFieldLimit = -1000
    upperFieldLimit = 1000
    steps = 100
    
    #%% Start up code    
        
    # Teorethical values for field/current ration
    xTeo = 0.5
    yTeo = 2.5
    zTeo = 0.5
    # opening MCU comunication
    COM = COMdetect()

    serialObj = createSerialObj(COM)
    
    # Opening the MCU comunication channel
    setupMCU(serialObj, samplesPerMean, timeBetweenSamples)
    sleep(0.1)
    startupCoilsPolarity(serialObj)
    
    # Opening PS comunication channel
    resource_name = 'USB0::0x1AB1::0x0E11::DP8A203800261::0::INSTR'   
    # specific for this dp800, you can find to another using
    '''
    rm = visa.ResourceManager() # To connect the wraper to the USB driver
    print(rm.list_resources_info()) # to take the resource name
    '''
    
    # Creating VISA objects
    rm, dp800 = startUpPowerSupply(resource_name)

#%% Rotation matrix
    
    rotationMatrix, CurrentToField, FieldToCurrent, er = rotationMatrixCalculator(dp800, serialObj, [xTeo,yTeo,zTeo])
    
    print("field/current ration error (%) for each coil")
    print(er)

#%% Setup of current manangers
    fData = getMeasurement(serialObj)
    zeroField = np.matmul(rotationMatrix, fData)
    
    coilCurrentCalculatorObj = [(CurrentCalculatorObj(i+1, zeroField[i], FieldToCurrent[i], CurrentToField[i])) for i in range(0,3)]
    
#%% Setting the desired field
    dataManager = storeDataObj(rotationMatrix)
    
    for i in range(2,-1,-1):
        fieldMeasurement, current, control = setField(dp800, serialObj, coilCurrentCalculatorObj[i], samplingTime*gain, float(0), rotationMatrix)
        dataManager.storeData(fieldMeasurement, current, i+1,zeroField[i], control)

    print("zeroField :\n"+str(zeroField))
    print("fieldMeasurement : \n"+str(fieldMeasurement))
    #-----------
    
    if pattern == 'straight':
        innerCoilFieldVector = np.linspace(lowerFieldLimit, upperFieldLimit, steps)    
        for j in range(0, len(innerCoilFieldVector)):
            # Send the command to set the current
            fieldMeasurement, current, control = setField(dp800, serialObj, coilCurrentCalculatorObj[1], samplingTime*gain, float(innerCoilFieldVector[j]), rotationMatrix, breakCondition = 0.5, maxIterations = 40)
            dataManager.storeData(fieldMeasurement, current, 2,zeroField[1], control)
            
            print("fieldMeasurement : \n"+str(fieldMeasurement))
            
            if (innerCoilFieldVector[j] != 0):
                fieldError = np.linalg.norm((fieldMeasurement[1] - innerCoilFieldVector[j])/innerCoilFieldVector[j])*100
            else:
                fieldError = float('inf')
            print("error (%) between desired and achieved field: \n"+str(fieldError))
    elif pattern == 'Circular':
        radius = 200
        size = 200
        teta = np.linspace(0,2*np.pi,size)
        innerCoilFieldVector = np.sin(teta)*radius
        midCoilFieldVector = np.cos(teta)*radius
        
        for j in range(0, len(innerCoilFieldVector)):
            # Send the command to set the current

            fieldMeasurement, current, control = setField(dp800, serialObj, coilCurrentCalculatorObj[1], samplingTime*gain, float(innerCoilFieldVector[j]), rotationMatrix, breakCondition = 0.5, maxIterations = 40)
            fieldMeasurement2, current2, control2 = setField(dp800, serialObj, coilCurrentCalculatorObj[2], samplingTime*gain, float(midCoilFieldVector[j]), rotationMatrix, breakCondition = 0.5, maxIterations = 40)
            
            dataManager.storeData(fieldMeasurement, current, 2,zeroField[1], control)
            dataManager.storeData(fieldMeasurement2, current2, 3,zeroField[2], control2)
            
            print("fieldMeasurement : \n"+str(fieldMeasurement))
            
    else:
        print("Please choose a existing parttern")
    #------------
        
    dataManager.createCSVfile(fileDir, fileName)
    
    #%% Closing the resources and file
    
    closeSerialObj(serialObj)
    closingPowerSupplyChannel(dp800, rm)
    
    #%% Closing the resources and file if something goes wrong in the execution of the program
except Exception as error:

    print(error)
    
    closeSerialObj(serialObj)
    closingPowerSupplyChannel(dp800, rm)

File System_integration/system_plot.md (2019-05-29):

```python
# -*- coding: utf-8 -*-
"""
Created on Wed Apr  3 16:55:50 2019

@author: aurelio
"""
import csv, matplotlib.pyplot as plt
from auxLib import getDataFromReader

#%% User code

csvPath = "./csvData/"
csvFileName = "fieldsNcurrents2"

#%%

fileField = csvPath + csvFileName + ".csv"
file = open(fileField, 'r')
reader = csv.reader(file, delimiter=';', quoting=csv.QUOTE_NONE)
floatData, channel, zeroField, ue, ue2 = getDataFromReader(reader, 1)

current = [list(),list(),list()]
aux = [0,0,0]
for i in range(0,len(floatData[3])):
    if channel[i] == 1:
        aux[0] = floatData[3][i]
    if channel[i] == 2:
        aux[1] = floatData[3][i]
    if channel[i] == 3:
        aux[2] = floatData[3][i]
        
    current[0].append(aux[0])
    current[1].append(aux[1])
    current[2].append(aux[2])

t = list(range(1,len(floatData[0])+1,1))

fig = plt.figure(figsize=(14,14), dpi=100)
fig.suptitle('Field x, y, z and current i', fontsize=20)

AXS = [fig.add_subplot(2,2,i, axisbelow=True) for i in range(1,5)]

subPlot = AXS

[[subPlot[i].set_xlabel('sample')] for i in range(0,4)]
subPlot[0].set_ylabel('x (uT)')
subPlot[1].set_ylabel('y (uT)')
subPlot[2].set_ylabel('z (uT)')
subPlot[3].set_ylabel('i (mA)')

[[subPlot[i].set_xlim([min(t)-1, max(t)+1])] for i in range(0,4)]
[[subPlot[i].set_ylim([min(floatData[i])-1,max(floatData[i])+1])] for i in range(0,4)]

subPlot[0].plot(t, floatData[0], color = 'r')
subPlot[1].plot(t, floatData[1], color = 'k')
subPlot[2].plot(t, floatData[2], color = 'm')
#subPlot[3].plot(t, floatData[3], color = 'b')
subPlot[3].plot(t, current[0], color = 'r')
subPlot[3].plot(t, current[1], color = 'k')
subPlot[3].plot(t, current[2], color = 'm')

fig.legend(["x", "y", "z","ix","iy","iz"])

fieldModules = list()

[[fieldModules.append(float((floatData[0][i]**2 + floatData[1][i]**2 + floatData[2][i]**2)**(1/2)))]for i in range(0, len(floatData[0]))]

fig3 = plt.figure(figsize = (12,12))
fig3.suptitle('Field module (uT) by sample', fontsize=20)

plt.plot(range(0,len(fieldModules)),fieldModules)

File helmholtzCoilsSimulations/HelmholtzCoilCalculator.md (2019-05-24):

```python
# -*- coding: utf-8 -*-
"""
This is a template that simulate a 3D helmholtz coil
in field amplitude and angle, it shows the 3D model of the 3D Coil

Author: Tarcis Becher
"""
#%% imports
import numpy as np
import magpylib as magpy
from magpylibUtils import constructAccess, coilDesign, plotBxyz

np.set_printoptions(suppress=True)

#%% Configuration of the coils

# via datasheet AWG23 https://docs-emea.rs-online.com/webdocs/157f/0900766b8157f396.pdf

# ----------------------------------------------------------#
# 1 2 3 4 5 6 -> LoopsInEachEvenLayer = 6                   #
#|-----------|                                              #
#|0 0 0 0 0 0| even                                         #
#| 0 0 0 0 0 | odd                                          #
#|0 0 0 0 0 0| even (always start with even layer)          #
#|-----------|                                              #
# *cross-cut of the windings where each "0" is a winding    #
#-----------------------------------------------------------#

# have to use a little bit bigger value than wireExternalDiameter, if not, the wire will not fit inside
AllCoilsWireDiameter = (0.56 + 0.047)*1.09   # Wire diameter in mm (from dataSheet)

minRes = 0.06736                            # Ohms/m (from dataSheet)
nominal = 0.06940                           # Ohms/m (from dataSheet)
maxRes = 0.07153                            # Ohms/m (from dataSheet)

wireResistence = maxRes                     # Ohms/m (from dataSheet)

# z First Coil configuration

zInitialValueCoilDiameter = 80 # Initial value for the function that calculates the precise diameter

zCoilCurrent = 0.5             # Amperes
zLoopsInEachEvenLayer = 10     # The number of loops in each layer
zEvenLayers = 7                # The evenlayers always have to be equal to oddLayers or oddLayers + 1
zOddLayers = 7
zDesiredField = 1.25           # The desired field in the center of the Helmholtz coil
zColor = 'k'

# y Second Coil configuration

yCoilCurrent = 0.5             # Amperes
yLoopsInEachEvenLayer = 6      # The number of loops in each layer
yEvenLayers = 3                # The evenlayers always have to be oddLayers + 1 or equal oddLayers
yOddLayers = 3
yDesiredField = 0.25           # The desired field in the center of the Helmholtz coil
yColor = 'k'

# x Third Coil configuration

xCoilCurrent = 0.5             # Amperes
xLoopsInEachEvenLayer = 7      # The number of loops in each layer
xEvenLayers = 3                # The evenlayers always have to be oddLayers + 1 or equal oddLayers
xOddLayers = 3
xDesiredField = 0.25           # The desired field in the center of the Helmholtz coil
xColor = 'k'

ZDESIGN = True
YDESIGN = True
XDESIGN = True

ZCOILPLOT = True
ZCOILSCONNECTORPLOT = False
YCOILPLOT = True
YCOILSCONNECTORPLOT = False
XCOILPLOT = True
XCOILSCONNECTORPLOT = False
DISPSYS = True

# xCoil - The collection with the first coil in the 'z' orientation
# yCoil - The collection with the second coil in the 'y' orientation
# xCoil - The collection with the second coil in the 'x' orientation
# connectorsCollection - The collection with all the access together
# zyxCoil - The collection with the coils all together
# zyxCoilandAcess - The collection with the entire system

# some setup for desiredCoilDiameter function
nIteration = 100
relativeDistance = 0.33333

# --------------------------------------------------------------------------
#%% DESIGN OF THE MAIN AXIS HELMHOLTZ COIL ('z') -----------------------------------------------------------------------------------------------
if ZDESIGN:

    zCoil, zCoilIntDiameter, zCoilExtDiameter, zCoilResistence, zCoilMaxPower, zWireLenghtMeters = coilDesign(nIteration = 40,
                                                                                                              initialValue = zInitialValueCoilDiameter,
                                                                                                              desiredField = zDesiredField, 
                                                                                                              I = zCoilCurrent, 
                                                                                                              wireDiameter=AllCoilsWireDiameter, 
                                                                                                              loopsInEachEvenLayer=zLoopsInEachEvenLayer, 
                                                                                                              evenLayers=zEvenLayers, oddLayers=zOddLayers, 
                                                                                                              orientation='z',
                                                                                                              relativeDistance = 1/3,
                                                                                                              maxError = 0.001, #%
                                                                                                              color = zColor,
                                                                                                              wireResistence = wireResistence)
    
    Bcenter = zCoil.getB([0,0,0.000001])   

    print('\nFor "z", getB([0,0,0]) = ',Bcenter ,' mT:')
    print('Internal Distance between coil = ',zCoilIntDiameter/2,' mm')
    print('Coil internal diameter = ',zCoilIntDiameter,' mm')
    print('Coil width = ', (AllCoilsWireDiameter*zLoopsInEachEvenLayer), 'mm') 
    print('min Coil height = ', (zCoilExtDiameter - zCoilIntDiameter), 'mm')  
    print('Coil resistence ~= '+ str(zCoilResistence) +' ohms' )
    print('Coil power dissipation ~= '+ str(zCoilMaxPower) +' W')
    print('Wire lenght necessary to construct the coil ~= '+ str(zWireLenghtMeters) +' m')

    singleCoilWidth = 0
    
    connectorsCollection =  magpy.Collection()
    connectorsCollection =  constructAccess(I = zCoilCurrent, coilExtDiameter = zCoilExtDiameter, wireDiameter = AllCoilsWireDiameter, 
                           centralPointBetweenHelmCoils = [0,0,0], lengthBetweenCoils = zCoilIntDiameter/2, 
                           singleCoilWidth = singleCoilWidth, helmCoil = connectorsCollection, relativeDistance = relativeDistance)
    
# ------------------------------------------------------------------------------------------------------------------------------------------------
#%% DESIGN OF THE SECOND HELMHOLTZ COIL ('y') -----------------------------------------------------------------------------------------------
if YDESIGN:
        
    yCoil, yCoilIntDiameter, yCoilExtDiameter, yCoilResistence, yCoilMaxPower, yWireLenghtMeters = coilDesign(nIteration = 40,
                                                                                                              initialValue = zCoilExtDiameter,
                                                                                                              desiredField = yDesiredField, 
                                                                                                              I = yCoilCurrent, 
                                                                                                              wireDiameter=AllCoilsWireDiameter, 
                                                                                                              loopsInEachEvenLayer=yLoopsInEachEvenLayer, 
                                                                                                              evenLayers=yEvenLayers, oddLayers=yOddLayers, 
                                                                                                              orientation='y',
                                                                                                              relativeDistance = 1/3,
                                                                                                              maxError = 0.001, #%
                                                                                                              color = yColor,
                                                                                                              wireResistence = wireResistence)
    
    Bcenter = yCoil.getB([0,0,0.000001])   

    print('\nFor "y", getB([0,0,0]) = ',Bcenter ,' mT:')
    print('Internal Distance between coil = ',yCoilIntDiameter/2,' mm')
    print('Coil internal diameter = ',yCoilIntDiameter,' mm')
    print('Coil width = ', (AllCoilsWireDiameter*yLoopsInEachEvenLayer), 'mm') 
    print('min Coil height = ', (yCoilExtDiameter - yCoilIntDiameter), 'mm')  
    print('Coil resistence ~= '+ str(yCoilResistence) +' ohms' )
    print('Coil power dissipation ~= '+ str(yCoilMaxPower) +' W')
    print('Wire lenght necessary to construct the coil ~= '+ str(yWireLenghtMeters) +' m')
    
    connectorsCollection.rotate(90,[1,0,0],anchor=[0,0,0])
    connectorsCollection.rotate(180,[0,1,0],anchor=[0,0,0])
            
    connectorsCollection =  constructAccess(I = yCoilCurrent, coilExtDiameter = yCoilExtDiameter, wireDiameter = AllCoilsWireDiameter, 
                           centralPointBetweenHelmCoils = [0,0,0], lengthBetweenCoils = yCoilIntDiameter/2, 
                           singleCoilWidth = singleCoilWidth, helmCoil = connectorsCollection, relativeDistance = relativeDistance)
    
    connectorsCollection.rotate(180,[0,1,0],anchor=[0,0,0])
    connectorsCollection.rotate(-90,[1,0,0],anchor=[0,0,0])
    
# --------------------------------------------------------------------------------------------------

#%% DESIGN OF THE THIRD HELMHOLTZ COIL ('x') -----------------------------------------------------------------------------------------------
if XDESIGN:
    
    xCoil, xCoilIntDiameter, xCoilExtDiameter, xCoilResistence, xCoilMaxPower, xWireLenghtMeters = coilDesign(nIteration = 40,
                                                                                                              initialValue = yCoilExtDiameter,
                                                                                                              desiredField = xDesiredField, 
                                                                                                              I = xCoilCurrent, 
                                                                                                              wireDiameter=AllCoilsWireDiameter, 
                                                                                                              loopsInEachEvenLayer=xLoopsInEachEvenLayer, 
                                                                                                              evenLayers=xEvenLayers, oddLayers=xOddLayers, 
                                                                                                              orientation='x',
                                                                                                              relativeDistance = 1/3,
                                                                                                              maxError = 0.001, #%
                                                                                                              color = xColor,
                                                                                                              wireResistence = wireResistence)
    
    Bcenter = xCoil.getB([0,0,0.000001])   

    print('\nFor "x", getB([0,0,0]) = ',Bcenter ,' mT:')
    print('Internal Distance between coil = ',xCoilIntDiameter/2,' mm')
    print('Coil internal diameter = ',xCoilIntDiameter,' mm')
    print('Coil width = ', (AllCoilsWireDiameter*xLoopsInEachEvenLayer), 'mm') 
    print('min Coil height = ', (xCoilExtDiameter - xCoilIntDiameter), 'mm')  
    print('Coil resistence ~= '+ str(xCoilResistence) +' ohms' )
    print('Coil power dissipation ~= '+ str(xCoilMaxPower) +' W')
    print('Wire lenght necessary to construct the coil ~= '+ str(xWireLenghtMeters) +' m')    
        
    connectorsCollection.rotate(-90,[0,1,0],anchor=[0,0,0])
    
    connectorsCollection =  constructAccess(I = xCoilCurrent, coilExtDiameter = xCoilExtDiameter, wireDiameter = AllCoilsWireDiameter, 
                           centralPointBetweenHelmCoils = [0,0,0], lengthBetweenCoils = xCoilIntDiameter/2, 
                           singleCoilWidth = singleCoilWidth, helmCoil = connectorsCollection, relativeDistance = relativeDistance)
    
    connectorsCollection.rotate(90,[0,1,0],anchor=[0,0,0])
            
zyxCoil = magpy.Collection(xCoil,zCoil,yCoil)
zyxCoilandAcess = magpy.Collection(zyxCoil, connectorsCollection)
# ----------------------------------------------------------------------------------------------------------------------------------------------

#%%
    
if ZCOILPLOT:    
    plotBxyz(collectionToPlot = zCoil, plotBounds = [-10,10,-10,10], orientation = 'y',  orderMagnitude = 'uT',
             fieldDif = False, figureSize = [16,8], nPlotPoints = 10, xyz0 = 0, figureTittle = 'Main coil ("+z")\ny = 0', 
             compareToCenter = True)
    if ZCOILSCONNECTORPLOT:
        plotBxyz(collectionToPlot = connectorsCollection, plotBounds = [-10,10,-10,10], orientation = 'y',  orderMagnitude = 'uT',
                 fieldDif = False, figureSize = [16,8], nPlotPoints = 10, xyz0 = 0, figureTittle = 'Connectors field ("+z")\ny = 0', 
                 compareToCenter = True)

    zCoil.displaySystem()    
    
if YCOILPLOT:
    plotBxyz(collectionToPlot = yCoil, plotBounds = [-10,10,-10,10], orientation = 'x',  orderMagnitude = 'uT',
             fieldDif = False, figureSize = [16,8], nPlotPoints = 10, xyz0 = 0, figureTittle = 'Second coil ("+y")\nx = 0', 
             compareToCenter = True)
    if YCOILSCONNECTORPLOT:
        plotBxyz(collectionToPlot = connectorsCollection, plotBounds = [-10,10,-10,10], orientation = 'x',  orderMagnitude = 'uT',
                 fieldDif = False, figureSize = [16,8], nPlotPoints = 10, xyz0 = 0, figureTittle = 'Connectors field ("+y")\nx = 0', 
                 compareToCenter = True)

    yCoil.displaySystem()

if XCOILPLOT:
    plotBxyz(collectionToPlot = xCoil, plotBounds = [-10,10,-10,10], orientation = 'z',  orderMagnitude = 'uT',
             fieldDif = False, figureSize = [16,8], nPlotPoints = 10, xyz0 = 0, figureTittle = 'Third coil ("+x")\nz = 0', 
             compareToCenter = True)
    if XCOILSCONNECTORPLOT:
        plotBxyz(collectionToPlot = connectorsCollection, plotBounds = [-10,10,-10,10], orientation = 'z',  orderMagnitude = 'uT',
                 fieldDif = False, figureSize = [16,8], nPlotPoints = 10, xyz0 = 0, figureTittle = 'Connectors field ("+x")\nz = 0', 
                 compareToCenter = True)

    xCoil.displaySystem()
    
if DISPSYS:
    connectorsCollection.displaySystem()
    zyxCoil.displaySystem()
    zyxCoilandAcess.displaySystem()

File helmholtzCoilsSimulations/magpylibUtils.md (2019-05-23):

```python
# -*- coding: utf-8 -*-
"""
Created on Tue Feb  5 11:01:56 2019

@author: Tarcis feat. Lucas

Helmholtz project auxiliar library

air permeability = 1.25663753e10−6

"""
import numpy as np
import magpylib as magpy
import matplotlib.pyplot as plt
from numpy import array,linspace,arange,sin,cos,tan,sqrt,r_,c_,pi,exp,sign,amax,amin,arctan,meshgrid,mean,polyfit,poly1d,std,dot,log,log10,logspace,arccos
#import gxPackage_v03 as gx
#import plotConfig_v18 as pconfig 
from numpy.linalg import norm
import datetime
import time

#%% coil function
def coil(color = 'k', I = 1, coilIntDiameter = 1, referencePosition=[0,0,0], wireDiameter=1, 
         loopsInEachEvenLayer=1, evenLayers = 1, oddLayers = 1, collectionToAdd = magpy.Collection()):
    """ 
    Return the model of a rolled coil around the 'z' axis.
    
    Parameters
    ----------
    I : float
        The Coil Current in Amperes.
    coilIntDiameter : {non-zero int}
        The Diameter of the coil's inner loops, in mm.
    referencePosition : List, default [0,0,0]
        A List containing 3 coordinates.
    wireDiameter : float, default 1
        Diameter of the coil wire in mm.
    loopsInEachEvenLayer : non-zero integer, default 1 
        How many loops in a single even layer
    evenLayers : integer, default 1
        Integer number of even layers.
    oddLayers : integer, default 1
        Integer number of odd layers.
    collectionToAdd : Magpy Collection, default empty
        Append coil source to a magpy collection.
    
    Example
    ---------
    test = coil(I = 4, coilIntDiameter = 77.26 , referencePosition=[0,0,0], wireDiameter=1.59, 
                loopsInEachEvenLayer=3, evenLayers = 3, oddLayers = 3, collectionToAdd = magpy.Collection())
    test.displaySystem()
    
    """

    # Initialization for the loop
    even = True                                                     # Flag if the coil rolling is in even format
    singleCoilWidth = wireDiameter*loopsInEachEvenLayer   
    centerPosition = referencePosition[2]                                    # The center position of the coil in Z
    initPosEven = centerPosition - singleCoilWidth/2 + wireDiameter/2     # Initial position in the 'even' form of rolling the coil
    initPosOdd = centerPosition - singleCoilWidth/2 + wireDiameter        # Initial position in the 'odd' form of rolling the coil
    stepPos = wireDiameter                                          # The position increment
    finalPosEven = centerPosition + singleCoilWidth/2 - wireDiameter/2 + stepPos    # Final position in the 'even' form of rolling the coil
    finalPosOdd = centerPosition + singleCoilWidth/2 - wireDiameter + stepPos     # Final position in the 'odd' form of rolling the coil
    stepDiameter = 2*(wireDiameter**2 - (wireDiameter/2)**2)**0.5   # The diameter increment
    subLoops = np.int64(singleCoilWidth/wireDiameter)                     # The max value of the loops in the 'even' rolling, the odd max value is (subLoops - 1)
    coilIntDiameter += wireDiameter
    
    if loopsInEachEvenLayer == 1:
        nLoops = evenLayers + oddLayers
    else:
        nLoops = loopsInEachEvenLayer*evenLayers + (loopsInEachEvenLayer-1)*oddLayers        # Total number of loops in each coil   
    # ----------------------------

    # Starting to roll the coil
    while nLoops > 0:                                   # loop that counts the number of wireLoops already done
        if (even == 1) | (singleCoilWidth == wireDiameter):                                                    # The statement that says if the rolling is in the 'even' or 'odd' form
            zs = np.arange(initPosEven, finalPosEven, stepPos)      # The 'zs' is the variable that will be used for rolling loop position
            for n in range(0,subLoops):                             
                coilLoop = magpy.source.current.Circular(curr=I, color = color, dim=coilIntDiameter,pos=[0,0,zs[n]])
                collectionToAdd.addSources(coilLoop)
                nLoops = nLoops - 1
                if nLoops <= 0:
                    break
            even = False
            coilIntDiameter = coilIntDiameter + stepDiameter
            
        else:                                              # The statement that says if the rolling is in the 'even' or 'odd' form
            zs = np.arange(initPosOdd, finalPosOdd, stepPos)      # The 'zs' is the variable that will be used for rolling loop position
            for n in range(0,subLoops-1):
                coilLoop = magpy.source.current.Circular(curr=I, color = color, dim=coilIntDiameter,pos=[0,0,zs[n]])            
                collectionToAdd.addSources(coilLoop)
                nLoops = nLoops - 1
                if nLoops <= 0:
                    break
            even = True
            coilIntDiameter = coilIntDiameter + stepDiameter
            
    return collectionToAdd
# -----------------------------------------------------------------------------------------------------------------------------------------------------------
#%% ConstrucAcess function 
def constructAccess( I = 4, centralPointBetweenHelmCoils = [0,0,0], coilExtDiameter = 1, relativeDistance = 1, 
                    wireDiameter = 1, singleCoilWidth = 1, lengthBetweenCoils = 1, helmCoil = magpy.Collection()):
    
    """
    Returns a collection with the wires access in 'x' axis orientation
    to the coils of a helmholtz collection with 'z' field orientation
    
    Parameters
    ----------
    I : float
        The Coil Current in Amperes.
    centralPointBetweenHelmCoils : integer, default 1
        Integer number of odd layers.
    coilExtDiameter : float
        The external diameter of one of the helmholtz coils, in mm.
    relativeDistance : float 0~1, default 1
        The porcentage of the 1.5*coilExtDiameter distance from the 
        centralPointBetweenHelmCoils that the wire will split to the coils
    wireDiameter : float, default 1
        Diameter of the coil wire in mm.
    singleCoilWidth : float, default 1 
        Width of a single coil of helmholtz coil, in mm
    lengthBetweenCoils : float, default 1
        The internal length between the two coils of the helmholtz coil
    helmCoil : Magpy Collection, default empty
        Append the wires to a magpy collection.
    
    Example
    ---------
    test = constructAccess( I = 4, centralPointBetweenHelmCoils = [0,0,0], coilExtDiameter = 1, relativeDistance = 0.5, 
                    wireDiameter = 1, singleCoilWidth = 1, lengthBetweenCoils = 1, helmCoil = magpy.Collection()):
    
    test.displaySystem()
    """
    
    # distance from the centralPointBetweenHelmCoils to the center of one coil of Helmholtz coil
    halfCoillengthBetweenCoils = (lengthBetweenCoils + singleCoilWidth)/2
                                 
    # Initializing the statingPoint of the wires with the central point of the coil + some distance relative to the coilIntDiameter
    wiresStartingPoint = centralPointBetweenHelmCoils                                        
    wiresStartingPoint[0] += 1.5*coilExtDiameter   
    
    #  |
    #
    #
    vector = [[wiresStartingPoint[0],wiresStartingPoint[1], wireDiameter +  wiresStartingPoint[2]], [wiresStartingPoint[0]*relativeDistance,0, wireDiameter] ]      
    line = magpy.source.current.Line(curr=I,vertices=vector)
    helmCoil.addSources(line)
    
    #  _|
    # 
    # 
    vector = [vector[1], [vector[1][0], vector[1][1], vector[1][2] + halfCoillengthBetweenCoils]]
    line = magpy.source.current.Line(curr=I,vertices=vector)
    helmCoil.addSources(line)
    
    #  _|
    # |
    # |
    vector = [vector[1], [coilExtDiameter/2 - wireDiameter, vector[1][1], vector[1][2]]]
    line = magpy.source.current.Line(curr=I,vertices=vector)
    helmCoil.addSources(line)
    
    #  _|
    # | 
    # ||
    vector = [[vector[1][0], vector[1][1], vector[1][2] - wireDiameter], [vector[0][0] -wireDiameter, vector[0][1], vector[0][2] - wireDiameter]]
    line = magpy.source.current.Line(curr=I,vertices=vector)
    helmCoil.addSources(line)
    
    # going to the other side
    #  _|
    # | __
    # ||
    vector = [vector[1], [vector[1][0], vector[1][1], -vector[1][2]]]
    line = magpy.source.current.Line(curr=I,vertices=vector)
    helmCoil.addSources(line)
    
    #  _|
    # | __
    # || |
    vector = [vector[1], [coilExtDiameter/2 - wireDiameter, vector[1][1], vector[1][2]]]
    line = magpy.source.current.Line(curr=I,vertices=vector)
    helmCoil.addSources(line)
    
    #  _|
    # | __ |
    # || ||
    vector = [[vector[1][0], vector[1][1], vector[1][2] - wireDiameter], [vector[0][0] + wireDiameter, vector[0][1], vector[0][2] - wireDiameter]]
    line = magpy.source.current.Line(curr=I,vertices=vector)
    helmCoil.addSources(line)
    
    #  _|  _
    # | __ |
    # || ||
    vector = [vector[1], [wiresStartingPoint[0]*relativeDistance,0, -wireDiameter]]
    line = magpy.source.current.Line(curr=I,vertices=vector)
    helmCoil.addSources(line)
    
    #  _| |_
    # | __ |
    # || ||
    vector = [[wiresStartingPoint[0]*relativeDistance,0, -wireDiameter], [wiresStartingPoint[0],wiresStartingPoint[1], -wireDiameter +  wiresStartingPoint[2]]]
    line = magpy.source.current.Line(curr=I,vertices=vector)
    helmCoil.addSources(line)
    
    return helmCoil

# -----------------------------------------------------------------------------------------------------------------------------------------------------------
#%% helmholtzCoil function 
def helmholtzCoil(color = 'k', collectionToAdd = 'NULL', I = 1, coilIntDiameter = 1, wireDiameter=1, loopsInEachEvenLayer=1, evenLayers=1, oddLayers=1, 
                  coilsDistance = 1, orientation = 'z', relativeDistance = 0.5,):
    ### (_TO DO: make the helmholtz coil do not touch each other_)
    """ 
    Generate and add 2 coils to a collection , with r distance (in mm) between both coils.
    Return a colection with the helmholtz coil inside
    
    Parameters
    ----------
    I : float
        The Helmhotz Coil Current in Amperes.
    coilIntDiameter : float
        The internal diameter of the coil in mm
    wireDiameter : float, optimizationional
        Diameter of the coil wire in mm.
    loopsInEachEvenLayer : non-zero integer, default 1 
        How many loops in a single even layer
    evenLayers : integer, default 1
        Integer number of even layers.
    oddLayers : integer, default 1
        Integer number of odd layers.
    collectionToAdd : Magpy Collection, default empty
        Append coil source to a magpy collection.
    coilsDistance : float , default 1
        Distance between the coil of the helmholtz coil
    orientation : {'x', 'y', 'z'}, optimizationional
        Change the orientation of the resulting coil having its center parallel with Plane X, Y, or Z.
    
    *OBS: the odd layers always must be evenLayers -1 or = evenLayers 
    
    Example
    ---------
    test = helmholtzCoil(I = 4, coilIntDiameter = 77.26, wireDiameter=1.59, 
                     loopsInEachEvenLayer=3, evenLayers=3, oddLayers=3, 
                     collectionToAdd=magpy.Collection(), coilsDistance = 77.26/2, orientation = 'x')
    test.displaySystem()
    """
    # seting some values to do the calculations after that
    if collectionToAdd == 'NULL':
        collectionToAdd=magpy.Collection()
        
    helmoltzRotationCenterXYZ = [0,0,0]
    singleCoilWidth = wireDiameter*loopsInEachEvenLayer 
    
    # doing the inverse rotations to change the helmhotz coil orientation (because this function only create the coil in 'z' orientation)
    if orientation == 'y':
        collectionToAdd.rotate(90,[1,0,0],anchor=helmoltzRotationCenterXYZ)
        collectionToAdd.rotate(90,[0,0,1],anchor=helmoltzRotationCenterXYZ)
    elif orientation == 'x':
        collectionToAdd.rotate(-90,[0,0,1],anchor=helmoltzRotationCenterXYZ)
        collectionToAdd.rotate(-90,[1,0,0],anchor=helmoltzRotationCenterXYZ)
    # ---------------------------------------------------------------------

    # construct the two coils of a helmholtz coil ----------------------------------------------------------------------------
    collectionToAdd = coil(I = I, color = color, coilIntDiameter = coilIntDiameter , referencePosition = [0,0,-coilsDistance/2-singleCoilWidth/2], 
                           wireDiameter=wireDiameter, loopsInEachEvenLayer=loopsInEachEvenLayer, 
                           evenLayers = evenLayers, oddLayers = oddLayers, collectionToAdd = collectionToAdd)
    collectionToAdd = coil(I = I, color = color, coilIntDiameter = coilIntDiameter , referencePosition = [0,0, coilsDistance/2+singleCoilWidth/2], 
                           wireDiameter=wireDiameter, loopsInEachEvenLayer=loopsInEachEvenLayer, 
                           evenLayers = evenLayers, oddLayers = oddLayers, collectionToAdd = collectionToAdd)
    # ------------------------------------------------------------------------------------------------------------------------
    '''
    # construct the access of supply wires to the two coils of a helmholtz coil ----------------------------------------------
    stepRadius = (wireDiameter**2 - (wireDiameter/2)**2)**0.5
    coilExtDiameter = coilIntDiameter + (wireDiameter + (evenLayers + oddLayers -1)*stepRadius)*2    # calculate the external diameter of the coil
    collectionToAdd = constructAccess(I = I, coilExtDiameter = coilExtDiameter, wireDiameter = wireDiameter, 
                                      centralPointBetweenHelmCoils = [0,0,0], lengthBetweenCoils = coilsDistance, 
                                      singleCoilWidth = singleCoilWidth, helmCoil = collectionToAdd, 
                                      relativeDistance = relativeDistance)
    # ------------------------------------------------------------------------------------------------------------------------
    '''
    
    # doing the rotations to change the helmhotz coil orientation
    if orientation == 'y':
        collectionToAdd.rotate(-90,[0,0,1],anchor=helmoltzRotationCenterXYZ)
        collectionToAdd.rotate(-90,[1,0,0],anchor=helmoltzRotationCenterXYZ)
    elif orientation == 'x':
        collectionToAdd.rotate(90,[1,0,0],anchor=helmoltzRotationCenterXYZ)
        collectionToAdd.rotate(90,[0,0,1],anchor=helmoltzRotationCenterXYZ)
    # ---------------------------------------------------------------------
        
    return collectionToAdd

# -----------------------------------------------------------------------------------------------------------------------------------------------------------
#%%
def plotBxyz(collectionToPlot, collectionToCompare = magpy.Collection(), plotBounds = [0,10,0,10], orientation = 'z', orderMagnitude = 'mT',
          fieldDif = False, figureSize = [10,8], nPlotPoints = 40, xyz0 = 0, figureTittle = 'Figure', compareToCenter = False, centerToCompare = [0,0,0]):
    
    """ 
    Plot in a 2d (x,z) in a y0 = constant graphic with 2 screens the [module %, angles º(related to the z direction)] 
    diference of the B in [0,0,0] and the other points of the graphic
    
    Parameters
    ----------
    collectionToPlot : Magpy Collection
        The collection used to caculate the plots
    plotBounds : float list [4]
        its the initial and final X and Z boundaries
        plotBound[0] = initialX, plotBound[1] = finalX
        plotBound[2] = initialZ, plotBound[3] = finalZ
    percent : bool
        If True, plot the percent diference relative to the B = [0,0,0] field
        If False, plot the true field in every point of the graphic
    optimization : bool
        If True, plot based in an eliptical line in the screen
        If False, plot every point related to the field in each point
    figureSize : list(integers) [2]
        Define the size of the entire figure
    nPlotPoints : integer
        Number of point that will be used to plot the figure in each axis
    y0 : float
        The plot made is an 2d 'z' by 'x', this select where in 'y' the plot will be made 
    figureTittle : string
        Define the entire figure tittle
        
    Example
    ---------
    test = helmholtzCoil(I = 4, coilIntDiameter = 77.26, wireDiameter=1.59, 
                         loopsInEachEvenLayer=3, evenLayers=3, oddLayers=3, 
                         collectionToAdd=magpy.Collection(), coilsDistance = 77.26/2, orientation = 'z')
    plotB(collectionToPlot = test, optimization= True, figureTittle = 'Test figure', nPlotPoints = 10, percent = True)
        
    test.displaySystem()
    """
    if orderMagnitude == 'uT':
        multiplier = 1000
    else:
        multiplier = 1
    # Here creates the screens and name the axis
    fig = plt.figure(figsize=(figureSize[0], figureSize[1]), dpi=80)
    fig.suptitle(figureTittle, fontsize=16)
    if compareToCenter:
        AXS = [fig.add_subplot(2,2,i, axisbelow=True) for i in range(1,5)]
        subPlot1,subPlot2,subPlot3,subPlot4 = AXS
    else:
        subPlot1 = fig.add_subplot(1,1,1, axisbelow=True)

    if orientation == 'y':
        subPlot1.set_xlabel('x axis (mm)')
        subPlot1.set_ylabel('z axis (mm)')
        
    elif orientation == 'x':
        subPlot1.set_xlabel('z axis (mm)')
        subPlot1.set_ylabel('y axis (mm)')
        collectionToPlot.rotate(90,[0,1,0],anchor=[0,0,0])
        collectionToCompare.rotate(90,[0,1,0],anchor=[0,0,0])
        collectionToPlot.rotate(90,[1,0,0],anchor=[0,0,0])
        collectionToCompare.rotate(90,[1,0,0],anchor=[0,0,0])
        
    elif orientation == 'z':
        subPlot1.set_xlabel('y axis (mm)')
        subPlot1.set_ylabel('x axis (mm)')
        collectionToPlot.rotate(-90,[0,1,0],anchor=[0,0,0])
        collectionToCompare.rotate(-90,[0,1,0],anchor=[0,0,0])
        collectionToPlot.rotate(-90,[0,0,1],anchor=[0,0,0])
        collectionToCompare.rotate(-90,[0,0,1],anchor=[0,0,0])

    # Here the process to create the plot arrays
    xs = linspace(plotBounds[0],plotBounds[1],nPlotPoints)
    zs = linspace(plotBounds[2],plotBounds[3],nPlotPoints)
        
    X,Z = meshgrid(xs,zs)
    
    # Here the process to take the points of the amplitude error and degree error
    Bs = array([[collectionToPlot.getB([xs[x],xyz0,zs[z]]) for x in range(0,len(xs))] for z in range(0,len(zs))])
    Bs = Bs*multiplier
    amp = Bs[:,:,2]
    
    if fieldDif:
        Bs2 = array([[collectionToCompare.getB([xs[x],xyz0,zs[z]]) for x in range(0,len(xs))] for z in range(0,len(zs))])
        Bs2 = Bs2*multiplier
        
        if orientation == 'x':
            amp2 = Bs2[:,:,2]
            #subPlot1.set_title('shows the % difference\n B1tc and B2tp, relative to B2tp \n(comparition in "y" orientation)')
            # shows the 'y' comparation
        elif orientation == 'z':
            amp2 = Bs2[:,:,2]
            #subPlot1.set_title('shows the % difference\n B1tc and B2tp, relative to B2tp \n(comparition in "x" orientation)')
            # shows the 'x' comparation
        elif orientation == 'y':
            amp2 = Bs2[:,:,2]
            #subPlot1.set_title('shows the % difference\n B1tc and B2tp, relative to B2tp \n(comparition in "z" orientation)')
            # shows the 'z' comparation
        ampDif = np.abs(amp2-amp)/amp
        subPlot1.contourf( X, Z, ampDif,10,cmap=plt.cm.jet)
        cp=subPlot1.contour( X, Z, ampDif,30,colors=('k','k'),linestyles = ('-','-'),linewidths=(1,1))
        subPlot1.clabel(cp, fontsize=10, inline=True,fmt= '%4.3f') 
    
    elif compareToCenter:
        # calculating the diffence of the the comparing point to the whole map
        Bcenter = collectionToPlot.getB(centerToCompare)
        Bcenter = Bcenter*multiplier
        Bs = array([[collectionToPlot.getB([xs[x],xyz0,zs[z]]) for x in range(0,len(xs))] for z in range(0,len(zs))])
        Bs = Bs*multiplier
        BsNorm = ((Bs[:,:,0])**2 + (Bs[:,:,1])**2 + (Bs[:,:,2])**2 )**0.5
        BcenterNorm = ((Bcenter[0])**2 + (Bcenter[1])**2 + (Bcenter[2])**2 )**0.5
        
        normDif = (BsNorm-BcenterNorm)/BcenterNorm*100
        # ---------------------------------------------------------------------------
        # Here the process to actualy plot int the screen
        subPlot1.set_title('B vector amplitude Error realative to the "center" (%)')
        subPlot1.contourf( X, Z, normDif,10,cmap=plt.cm.jet)
        cp=subPlot1.contour( X, Z, normDif,30,colors=('k','k'),linestyles = ('-','-'),linewidths=(1,1))
        subPlot1.clabel(cp, fontsize=10, inline=True,fmt= '%4.3f')
        
        # Here calculate the angle to plot
        
        if orientation == 'y':
            subPlot1.set_xlabel('.')
            subPlot2.set_xlabel('.')
            subPlot2.set_ylabel('z axis (mm)')
            subPlot3.set_xlabel('x axis (mm)')
            subPlot3.set_ylabel('z axis (mm)')
            subPlot4.set_xlabel('x axis (mm)')
            subPlot4.set_ylabel('z axis (mm)')
            Bsx = Bs[:,:,0]
            Bsy = Bs[:,:,1]
            Bsz = Bs[:,:,2]
        
        elif orientation == 'x':
            subPlot1.set_xlabel('.')
            subPlot2.set_xlabel('.')
            subPlot2.set_ylabel('y axis (mm)')
            subPlot3.set_xlabel('z axis (mm)')
            subPlot3.set_ylabel('y axis (mm)')
            subPlot4.set_xlabel('z axis (mm)')
            subPlot4.set_ylabel('y axis (mm)')
            Bsx = Bs[:,:,1]
            Bsy = Bs[:,:,2]
            Bsz = Bs[:,:,0]
        
        elif orientation == 'z':
            subPlot1.set_xlabel('.')
            subPlot2.set_xlabel('.')
            subPlot2.set_ylabel('x axis (mm)')
            subPlot3.set_xlabel('y axis (mm)')
            subPlot3.set_ylabel('x axis (mm)')
            subPlot4.set_xlabel('y axis (mm)')
            subPlot4.set_ylabel('x axis (mm)')
            Bsx = Bs[:,:,2]
            Bsy = Bs[:,:,0]
            Bsz = Bs[:,:,1]
        
        if orderMagnitude == 'uT':
            subPlot2.set_title('x component (uT)')
            subPlot3.set_title('y component (uT)')
            subPlot4.set_title('z component (uT)')
            
        else:
            subPlot2.set_title('x component (mT)')
            subPlot3.set_title('y component (mT)')
            subPlot4.set_title('z component (mT)')
        #print(Bs)
        subPlot2.contourf( X, Z, Bsx,10,cmap=plt.cm.jet)
        cp=subPlot2.contour( X, Z, Bsx,30,colors=('k','k'),linestyles = ('-','-'),linewidths=(1,1))
        subPlot2.clabel(cp, fontsize=10, inline=True,fmt= '%4.3f')    

        subPlot3.contourf( X, Z, Bsy,10,cmap=plt.cm.jet)
        cp=subPlot3.contour( X, Z, Bsy,30,colors=('k','k'),linestyles = ('-','-'),linewidths=(1,1))
        subPlot3.clabel(cp, fontsize=10, inline=True,fmt= '%4.3f')       

        subPlot4.contourf( X, Z, Bsz,10,cmap=plt.cm.jet)
        cp=subPlot4.contour( X, Z, Bsz,30,colors=('k','k'),linestyles = ('-','-'),linewidths=(1,1))
        subPlot4.clabel(cp, fontsize=10, inline=True,fmt= '%4.3f')         
    else:
        if orderMagnitude == 'uT':
            subPlot1.set_title('B vector amplitude (uT)')
        else:
            subPlot1.set_title('B vector amplitude (mT)')
        subPlot1.contourf( X, Z, amp,10,cmap=plt.cm.jet)
        cp=subPlot1.contour( X, Z, amp,30,colors=('k','k'),linestyles = ('-','-'),linewidths=(1,1))
        subPlot1.clabel(cp, fontsize=10, inline=True,fmt= '%4.3f')
    
    if orientation == 'x':
        collectionToPlot.rotate(-90,[1,0,0],anchor=[0,0,0])
        collectionToCompare.rotate(-90,[1,0,0],anchor=[0,0,0])
        collectionToPlot.rotate(-90,[0,1,0],anchor=[0,0,0])
        collectionToCompare.rotate(-90,[0,1,0],anchor=[0,0,0])
        
    elif orientation == 'z':
        collectionToPlot.rotate(90,[0,0,1],anchor=[0,0,0])
        collectionToCompare.rotate(90,[0,0,1],anchor=[0,0,0])
        collectionToPlot.rotate(90,[0,1,0],anchor=[0,0,0])
        collectionToCompare.rotate(90,[0,1,0],anchor=[0,0,0])

#%% nextCoilMinimalDiameter function 
def nextCoilMinimalDiameter(coilExtDiameter = 1, coilExtlengthBetweenCoils = 1):
    """ 
    In more than 1d axis Helmholtz Coil context, it returns the minimal diameter 
    that the next axis Coil must have to fit the system, mechanicaly speaking
    
    Parameters
    ----------
    coilExtDiameter : float
        It's the previous helmholtz Coil External Diameter
    coilExtlengthBetweenCoils : float
        It's the length between the two coils of the previous helmholtz coil
        
    Example
    ---------
    test = helmholtzCoil(I = 4, coilIntDiameter = 77.26, wireDiameter=1.59, 
                         loopsInEachEvenLayer=3, evenLayers=3, oddLayers=3, 
                         collectionToAdd=magpy.Collection(), coilsDistance = 77.26/2, orientation = 'z')
    plotB(collectionToPlot = test, optimization= True, figureTittle = 'Test figure', nPlotPoints = 10, percent = True)
        
    test.displaySystem()
    """    
    
    teta = pi/6
    RecBase = np.cos(teta)*coilExtDiameter
    RecHeigth = coilExtlengthBetweenCoils
    newCoilIntDiameter = (RecHeigth**2 + RecBase**2)**0.5
        
    return newCoilIntDiameter

# -----------------------------------------------------------------------------------------------------------------------------------------------------------
#%% spiral function 
def spiral(diameter = 2, spiralExtremities = [0,1], nPoints = 40, nTurns = 4, I = 1, startingSpiralAng = 0, 
           rotationSense = 1, referencePosition = [0,0,0]):
    
    """ 
    Returns an object that contains a spiral line field
    
    Parameters
    ----------
    diameter : float
        Diameter of the spiral
    spiralExtremities : list (float) [2]
        The beginning [0], and the end [1] in 'z' orientation of the spiral
    nPoints : float
        Number of points in the spiral, greater the number, more "realistic" model
        of a spiral you get
    nTurns : positive integer 
        Number of the turns that will have in your spiral
    I : float
        The current amplitude that will create the magnetic field
    startingSpiralAng : float (0~180)
        It's the starting angle of the spiral
    rotationSense : integer (-1,1)
        This multiply the angle, so the sense will be positive increasing or negative increasing
    referencePosition : list (float) [3]
        is the starting point where the spiral will be created, in 'z' orientation
          
    Example
    ---------
    test = spiral(diameter = 2, spiralExtremities = [0,4], nPoints = 40, nTurns = 4, I = 1, startingSpiralAng = 0, 
           rotationSense = 1, referencePosition = [1,1,1])
    test = magpy.Collection(test)
    test.displaySystem()
    """    
    
    # Creating the linear space wheres that will creates the spiral
    spiralExtremities = linspace(spiralExtremities[0],spiralExtremities[1],nPoints)
    phi = linspace(0,rotationSense*2*pi*nTurns,nPoints)
    
    # Creating the spiral around the 'z' axis
    vertices = [[diameter/2*cos(phi[i]),diameter/2*sin(phi[i]),spiralExtremities[i]] for i in range(0,nPoints)]
    spi = magpy.source.current.Line(curr=I,vertices=vertices, pos=referencePosition)
    spi.rotate(startingSpiralAng,[0,0,1],anchor=referencePosition)
    
    return spi

# -----------------------------------------------------------------------------------------------------------------------------------------------------------
#%% twistedPair function 
def twistedPair(diameter = 2, nPoints = 40, nTurns = 10, I = 4, collectionToAdd = magpy.Collection(), referencePosition= [0,0,0], end = [0,0,1]):
    
    """ 
    Returns a Collection that is a previous Collection with a twisted pair plus that
    *OBS: still have to fix the rotations
    
    Parameters
    ----------
    diameter : float
        Diameter of the spiral
    spiralExtremities : list (float) [2]
        The beginning [0], and the end [1] in 'z' orientation of the spiral
    nPoints : float
        Number of points in the spiral, greater the number, more "realistic" model
        of a spiral you get
    nTurns : positive integer 
        Number of the turns that will have in your spiral
    I : float
        The current amplitude that will create the magnetic field
    startingSpiralAng : float (0~180)
        It's the starting angle of the spiral
    rotationSense : integer (-1,1)
        This multiply the angle, so the sense will be positive increasing or negative increasing
    referencePosition : list (float) [3]
        is the starting point where the spiral will be created, in 'z' orientation
          
    Example
    ---------
    test = twistedPair(diameter = 2, nPoints = 40, nTurns = 4, I = 4, collectionToAdd = magpy.Collection(), referencePosition= [0,0,0], end = [0,0,3])
    test.displaySystem()
    
    """    
    
    # Find the rotations angles for the right positioning of the twisted pair ------------------------------
    spiralExtremities = np.zeros(2)
    spiralExtremities[0] = 0
    spiralExtremities[1] = ((end[0] - referencePosition[0])**2 + (end[1] - referencePosition[1])**2 + (end[2] - referencePosition[2])**2 )**0.5

    print(spiralExtremities[1])         # debug
    # *OBS: still have to fix the rotations
    """
    phi = -np.arccos((end[2] - referencePosition[2])/spiralExtremities[1])
    print(phi)                          # debug
    teta = np.arccos((end[0] - referencePosition[0])/spiralExtremities[1]/np.sin(phi))*180/pi
    print(teta)                         # debug
    phi = phi*180/pi
    
    # -------------------------------------------------------------------------------------
    
    # Doing the inverse rotations -------------------------------------
    collectionToAdd.rotate(-teta,[0,0,1],anchor=referencePosition)
    collectionToAdd.rotate(-phi,[1,0,0],anchor=referencePosition)
    # -------------------------------------------------------------------------------------
    """
    # Doing one spiral in the 'z' positive orientation
    spi = spiral(diameter = diameter, spiralExtremities = [spiralExtremities[0],spiralExtremities[1]], nPoints = nPoints, 
                 nTurns = nTurns, I = I, startingSpiralAng = 0, referencePosition = referencePosition)
    collectionToAdd.addSources(spi)

    # Doing the second spiral in the 'z' negative orientation
    spi = spiral(diameter = diameter, spiralExtremities = [spiralExtremities[1],spiralExtremities[0]], nPoints = nPoints, 
                 nTurns = nTurns, I = I, startingSpiralAng = 180, rotationSense = -1, referencePosition = referencePosition)
    collectionToAdd.addSources(spi)
    """
    # Doing the rotations -------------------------------------
    collectionToAdd.rotate(phi,[1,0,0],anchor=referencePosition)
    collectionToAdd.rotate(teta,[0,0,1],anchor=referencePosition)
    # -------------------------------------------------------------------------------------
    """
    return collectionToAdd

# -----------------------------------------------------------------------------------------------------------------------------------------------------------

def WhatTimeIsIt():
    justTime = str(datetime.datetime.now())
    #return justTime[0:22]
    return time.time()
#%% desiredCoilDiameter function 
def desiredCoilDiameter(nIteration = 1000, breakCondition = 0.005, desiredField = 1, initialValue = 0, 
                        I = 1, coilIntDiameter = 1, wireDiameter=1, loopsInEachEvenLayer=3, evenLayers=3, oddLayers=3, 
                        orientation='z', relativeDistance = 0.5):
    """ 
    Returns a Collection that is a previous Collection with a twisted pair plus that
    *OBS: still have to fix the rotations
    
    Parameters
    ----------
    nIteration : integer
        Determine how many iterations the loop will do
    breakCondition : float
        It's the B - Ba break condition
    coilIntDiameterStep : float
        The step that the coil diameter tested will increase or decrease
    desiredField : float
        The field amplitude value that the function will search for
    I : float
        The Helmhotz Coil Current in Amperes.
    coilIntDiameter : float
        The internal diameter of the coil in mm (initial value)
    wireDiameter : float, optimizationional
        Diameter of the coil wire in mm.
    loopsInEachEvenLayer : non-zero integer, default 1 
        How many loops in a single even layer
    evenLayers : integer, default 1
        Integer number of even layers.
    oddLayers : integer, default 1
        Integer number of odd layers.
    collectionToAdd : Magpy Collection, default empty
        Append coil source to a magpy collection.
    coilsDistance : float , default 1
        Distance between the coil of the helmholtz coil
    orientation : {'x', 'y', 'z'}, optimizationional
        Change the orientation of the resulting coil having its center parallel with Plane X, Y, or Z.
    
    *OBS: the odd layers always must be evenLayers -1 or = evenLayers 
    
    Example
    ---------
    test = twistedPair(diameter = 2, nPoints = 40, nTurns = 4, I = 4, collectionToAdd = magpy.Collection(), referencePosition= [0,0,0], end = [0,0,3])
    test.displaySystem()
    
    """    
    
    # Setting the initial values of B and Ba
    samplingTime = 100
    previousError = 0
    previousCoilIntDiameter = initialValue
    i = 0
    # The iteration loop that will find the correct HelmoltzCoil to get the I desired with B desired together
    while (1):

        coilIntDiameter = -previousError*samplingTime + previousCoilIntDiameter
        if coilIntDiameter < 0.1:
            coilIntDiameter = 0.1
        #b = WhatTimeIsIt()
        # Creates a new helmholtzCoil, to search for the right coilintDiameter value
        EmptyCol = magpy.Collection()
        Coil = helmholtzCoil(I = I, coilIntDiameter = coilIntDiameter, wireDiameter=wireDiameter, 
                             loopsInEachEvenLayer=loopsInEachEvenLayer, evenLayers=evenLayers, oddLayers=oddLayers, 
                             collectionToAdd=EmptyCol, coilsDistance = coilIntDiameter/2, orientation = orientation,
                             relativeDistance = relativeDistance)
        # --------------------------------------------------------------------------------------------
        #a = WhatTimeIsIt()
        #print(a-b)
        # Store the B in Ba and calculate the new B
        field = Coil.getB([0,0,0])
        if(orientation == 'z'):
            field = field[2]
        elif(orientation == 'y'):
            field = field[1]
        elif(orientation == 'x'):
            field = field[0]
        else:
            field = norm(field)
        
        error = desiredField - field
        #print(error)
        #print(coilIntDiameter)
        previousError  = error
        previousCoilIntDiameter = coilIntDiameter
        
        i += 1
        if i > nIteration:
            break
        if np.linalg.norm(error) < breakCondition:
            break
        #print(B)
    # -----------------------------------------------------------------------------------------------------
    
    return coilIntDiameter

 # Setting input values -------------------------------------------------------------------------------------------------------------------------
 
def coilDesign(nIteration = 40,
               initialValue = 0.1,
               desiredField = 0.1, 
               I = 0.1, 
               wireDiameter=0.6, 
               loopsInEachEvenLayer=5, 
               evenLayers=5, oddLayers=5, 
               orientation='z',
               relativeDistance = 1/3,
               maxError = 0.1,
               color = 'k',
               wireResistence = 0.5):

    # ----------------------------------------------------------------------------------------------------------------------------------------------
    # Finding the right coil internal diameter to have the desired field with the zCoilCurrent in A
    newCoilIntDiameter = desiredCoilDiameter(nIteration = nIteration, 
                                              breakCondition = desiredField*maxError/100, 
                                              initialValue = initialValue,
                                              desiredField = desiredField, 
                                              I = I, 
                                              coilIntDiameter = initialValue, 
                                              wireDiameter=wireDiameter, 
                                              loopsInEachEvenLayer=loopsInEachEvenLayer, 
                                              evenLayers=evenLayers, oddLayers=oddLayers, 
                                              orientation=orientation,
                                              relativeDistance = relativeDistance)
    # ---------------------------------------------------------------------------------------------

    # Constructing the desired coil ---------------------------------------------------------------
    Coil = helmholtzCoil(color = color,I = I, 
                           coilIntDiameter = newCoilIntDiameter, 
                           wireDiameter=wireDiameter, 
                           loopsInEachEvenLayer=loopsInEachEvenLayer, 
                           evenLayers=evenLayers, oddLayers=oddLayers, 
                           coilsDistance=newCoilIntDiameter/2, 
                           orientation=orientation, 
                           relativeDistance = relativeDistance)
    # --------------------------------------------------------------------------------------------- 
    
    # calculating the energy dissipation by joule effect --------------------------------------------------------------------------------------------
    coilExtDiameter = newCoilIntDiameter
    wireLenght = 0
    
    for i in range(0,evenLayers + oddLayers):
        if (i % 2) == 0:
            wireLenght += coilExtDiameter*pi*loopsInEachEvenLayer
        elif (i % 2) == 1:
            wireLenght += coilExtDiameter*pi*(loopsInEachEvenLayer-1)
        coilExtDiameter += ((3)**(1/2))*wireDiameter/2
    
    wireLenghtMeters = 2*wireLenght/1000
    coilResistence = wireResistence*wireLenghtMeters
    coilMaxPower = coilResistence*(I**2)

    return Coil, newCoilIntDiameter, coilExtDiameter, coilResistence, coilMaxPower, wireLenghtMeters

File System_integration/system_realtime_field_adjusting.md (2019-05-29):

```python
# -*- coding: utf-8 -*-
"""
py file that automatic sets the field of the 3DHC
"""
#%% Imports

import numpy as np
import matplotlib.pyplot as plt
from time import sleep
import csv
from auxLib import  updateCoilPolarity, rotationMatrixCalculator, storeDataObj, writeDataOnFile, CurrentCalculatorObj, setField, startupCoilsPolarity, closeFile, closeSerialObj, createAndOpenFile, WhatTimeIsIt, makeDir, createSerialObj, COMdetect, changeCoilPolarity, measurementNtransformation, setPowerSupplyChVoltage, setPowerSupplyAllChVoltage, setPowerSupplyAllChCurrent, setupMCU, closingPowerSupplyChannel, startUpPowerSupply, getMeasurement, setPowerSupplyChCurrent

# To show numbers in console in the raw representation
np.set_printoptions(suppress=True)
#%% Channel controller class
#closeSerialObj(serialObj)
try:
#if 1:
    #%% User code
    # Setup information to the microcontroller, must be in binary format "b'information'"
    samplesPerMean = b'30'
    timeBetweenSamples = b'1'
    gain = 1
    samplingTime = 0.2*gain
    
    desiredField = [0, 4, 3.6]
    
    plotRealTime = 1
    
    meanSize = 1
    nSamples = 25
    plotLim = 30
    
    maxPoints = 30000
    
    #%% Start up code    
        
    # opening MCU comunication
    COM = COMdetect()

    serialObj = createSerialObj(COM)
    
    # Opening the MCU comunication channel
    setupMCU(serialObj, samplesPerMean, timeBetweenSamples)
    sleep(0.1)
    startupCoilsPolarity(serialObj)
    
    # Opening PS comunication channel
    resource_name = 'USB0::0x1AB1::0x0E11::DP8A203800261::0::INSTR'
    rm, dp800 = startUpPowerSupply(resource_name)

#%% Rotation matrix
    
    rotationMatrix, CurrentToField, FieldToCurrent, er = rotationMatrixCalculator(dp800, serialObj, [0.5,2.5,0.5])

#%% ClosedLoop control
    #--------------------------------------------------------------------------------------------------------------------------------------------
    
    dp800.write("DISP:MODE NORM")
    index = 0
    supLim = 500
    iAnt = [0, 0, 0]
    eAnt = [0, 0, 0]
    i = [0, 0, 0]
    e = [0, 0, 0]
    
    plotData = np.zeros((3,nSamples))
    dataIndex = 0
    t = range(0, nSamples)
    plt.figure(figsize=(14,14), dpi=100)
    
    fData = getMeasurement(serialObj)
    zeroField = np.matmul(rotationMatrix, fData)
    
    coilCurrentCalculatorObj = [(CurrentCalculatorObj(i+1, zeroField[i], FieldToCurrent[i], CurrentToField[i])) for i in range(0,3)]
    
    iAnt = [coilCurrentCalculatorObj[0].calculateCurrent(0), coilCurrentCalculatorObj[1].calculateCurrent(0), coilCurrentCalculatorObj[2].calculateCurrent(0)]
    
    while(index < maxPoints):

        for j in range(0,3):
            i[j] = eAnt[j]*samplingTime + iAnt[j]
            if i[j] > supLim:
                i[j] = supLim
            if i[j] < -supLim:
                i[j] = -supLim
                
        i[1] = eAnt[1]*samplingTime/6 + iAnt[1]
        if i[1] > supLim:
            i[1] = supLim
        if i[1] < -supLim:
            i[1] = -supLim  
        updateCoilPolarity(serialObj, i[0], 1)
        updateCoilPolarity(serialObj, i[1], 2)
        updateCoilPolarity(serialObj, i[2], 3)
        
        setPowerSupplyChCurrent(dp800, 1, float(i[0]/1000))
        setPowerSupplyChCurrent(dp800, 2, float(i[1]/1000))
        setPowerSupplyChCurrent(dp800, 3, float(i[2]/1000)) 
        
        fData = getMeasurement(serialObj)
        currentField = np.matmul(rotationMatrix, fData)
        
        for j in range(0,3):
            e[j] = desiredField[j] - currentField[j]
            eAnt[j] = e[j]
            iAnt[j] = i[j]

        if plotRealTime:

            for u in range(0,3):
                plotData[u][dataIndex] = 0
                for h in range(1,meanSize):
                    if dataIndex-h < 0:
                        plotData[u][dataIndex] += plotData[u][nSamples-h]
                    else:
                        plotData[u][dataIndex] += plotData[u][dataIndex-h]
                plotData[u][dataIndex] =  currentField[u]  
                plotData[u][dataIndex] = plotData[u][dataIndex]/meanSize
                
            ''' 
            plotData[0][dataIndex] = currentField[0]
            plotData[1][dataIndex] = currentField[1]
            plotData[2][dataIndex] = currentField[2]
            '''
            if index != 0:
                plt.clf()
                plt.ylim(-plotLim,plotLim)
                plt.plot(t, plotData[0], 'r', label = 'x axis')
                plt.plot(t, plotData[1], 'b', label = 'y axis')
                plt.plot(t, plotData[2], 'm', label = 'z axis')
                plt.legend()
                plt.pause(0.001)
                
            dataIndex += 1    
            
            if dataIndex >= nSamples:
                dataIndex = 0

        index += 1
      
    #%% Closing the resources and file
    
    closeSerialObj(serialObj)
    closingPowerSupplyChannel(dp800, rm)
    
    #%% Closing the resources and file if something goes wrong in the execution of the program
except Exception as error:

    print(error)
    
    closeSerialObj(serialObj)
    closingPowerSupplyChannel(dp800, rm)

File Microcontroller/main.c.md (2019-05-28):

```C
/**
  ******************************************************************************
  * @file           : main.c
  * @brief          : UART comunication with I2C sensor control
  ******************************************************************************
  * @attention
  *
  * <h2><center>&copy; Copyright (c) 2019 STMicroelectronics.
  * All rights reserved.</center></h2>
  *
  * This software component is licensed by ST under BSD 3-Clause license,
  * the "License"; You may not use this file except in compliance with the
  * License. You may obtain a copy of the License at:
  *                        opensource.org/licenses/BSD-3-Clause
  *
  ******************************************************************************
  */

/* Includes ------------------------------------------------------------------*/

#include "main.h"
#include "lib_aux.h"

/* Private variables ---------------------------------------------------------*/
I2C_HandleTypeDef hi2c1;

SPI_HandleTypeDef hspi1;

TIM_HandleTypeDef htim2;

UART_HandleTypeDef huart2;

typedef enum dieBruter {
	WAIT_FOR_COMMAND = 0,
	SET_INNER_COIL_POLARITY,
	RESET_INNER_COIL_POLARITY,
	SET_MIDDLE_COIL_POLARITY,
	RESET_MIDDLE_COIL_POLARITY,
	SET_EXTERNAL_COIL_POLARITY,
	RESET_EXTERNAL_COIL_POLARITY,
	DO_MEASUREMENT,
	START_UP_POLARITY,
	CONTINUOUS_MEASUREMENT_STATE
}stateType;

/* Private function prototypes -----------------------------------------------*/
void SystemClock_Config(void);
static void MX_GPIO_Init(void);
static void MX_USART2_UART_Init(void);
static void MX_I2C1_Init(void);
static void MX_SPI1_Init(void);
static void MX_TIM2_Init(int count);

volatile unsigned int flagTIM2 = FALSE;

int askValue(const char* message);
int measurementReadyToRead();
void resetRxBuffer();
stateType verifyCommandRxBuffer();
int measurementProcedure();
void resetSSRBridge();
void resetExternalPolarity();
void setExternalPolarity();
void resetInnerPolarity();
void setInnerPolarity();
void resetMiddlePolarity();
void setMiddlePolarity();

int dataMeanSize;
int nTimerCount;

stateType state = WAIT_FOR_COMMAND;

unsigned int i = 0;
float xfValue = 0;
float yfValue = 0;
float zfValue = 0;
int middleFlag = 0;

float data[3];

int main(void)
{
  /* MCU Configuration--------------------------------------------------------*/

  /* Reset of all peripherals, Initializes the Flash interface and the Systick. */
  HAL_Init();

  /* Configure the system clock */
  SystemClock_Config();

  /* Initialize all configured peripherals */
  MX_GPIO_Init();
  MX_USART2_UART_Init();
  MX_I2C1_Init();
  MX_SPI1_Init();

  // Sensor configuration
  MMC3416verifyConection();
  configureMMC3416();

  resetMiddlePolarity();
  resetInnerPolarity();
  resetExternalPolarity();

  if (HAL_GPIO_ReadPin(GPIOA, GPIO_PIN_12))
  {
	  dataMeanSize = askValue("DataMeanSize?\n");
	  nTimerCount = askValue("nTimerCount?\n");
  }
  else
  {
	  dataMeanSize = 30;
  	  nTimerCount = 300;
  }

  MX_TIM2_Init(nTimerCount);
  HAL_TIM_Base_Start_IT(&htim2);

  if (!HAL_GPIO_ReadPin(GPIOA, GPIO_PIN_12)) // D2 pin, it's in pull up
  {
	  state = WAIT_FOR_COMMAND;
  }

  resetRxBuffer();

  while (1)
  {
	  if (flagTIM2)
	  {
		  switch(state) {

			 case WAIT_FOR_COMMAND  :
				state = verifyCommandRxBuffer();
				break;

			 case SET_INNER_COIL_POLARITY  :
				setInnerPolarity();
				state = WAIT_FOR_COMMAND;

				UART_transmit_message(aTxBuffer, "I Done\n");
				break;

			 case RESET_INNER_COIL_POLARITY  :
				resetInnerPolarity();
				state = WAIT_FOR_COMMAND;

				UART_transmit_message(aTxBuffer, "i Done\n");
				break;

			 case SET_MIDDLE_COIL_POLARITY  :
				setMiddlePolarity();
				state = WAIT_FOR_COMMAND;

				UART_transmit_message(aTxBuffer, "M Done\n");
				break;

			 case RESET_MIDDLE_COIL_POLARITY  :
				resetMiddlePolarity();
				state = WAIT_FOR_COMMAND;

				UART_transmit_message(aTxBuffer, "m Done\n");
				break;

			 case SET_EXTERNAL_COIL_POLARITY  :
				setExternalPolarity();
				state = WAIT_FOR_COMMAND;

				UART_transmit_message(aTxBuffer, "E Done\n");
				break;

			 case RESET_EXTERNAL_COIL_POLARITY  :
				resetExternalPolarity();
				state = WAIT_FOR_COMMAND;

				UART_transmit_message(aTxBuffer, "e Done\n");
				break;

			 case DO_MEASUREMENT  :
				if(!measurementProcedure())
				{
					state = WAIT_FOR_COMMAND;
				}
				break;

			 case START_UP_POLARITY  :

				resetExternalPolarity();
				resetInnerPolarity();
				resetMiddlePolarity();

				state = WAIT_FOR_COMMAND;
				UART_transmit_message(aTxBuffer, "S Done\n");

				break;
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

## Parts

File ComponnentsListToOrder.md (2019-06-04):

# Helmholtz Coil System components
### June 04, 2019 - *Thursday*

---

### To order:

---
  
[Eurocircuits Gmbh]:https://www.eurocircuits.com/
### Already ordered

-   *PCB's* - [Eurocircuits Gmbh] (191,81 eu)
  
##### Power Supply
-   *[DP-831A]* **[1]** - Power Supply
    -   *[PowerSupply Datasheet]*
    -   *[PowerSupply Programming Guide]*
    -   *[RIGOL support]*
##### Insulated Copper Wire
-   *[AWG 23]* **[1]** - Wire Standard
    -   *[AWG23 doc]*
-   *[AWG 22]* **[1]** - **Will not use this one**

##### Microcontroler
-   *[STM32L432KCU6]* **[2]** - Microcontroller ARM m4
    -   *[STM32L4 datasheet]*
    -   *[STM32L4 doc]*

##### Magnetic Sensors-   
-   *[MMC3416]* **[5]** - Magnetic Sensor $\pm$16 G
-   *[evalMMC3416]* **[2]** - Magnetic sensor **(Will use this one)**
    -   *[MMC3416 datasheet]*

-   *[evalLIS3MDL]* **[2]** - Magnetic sensor
    -   *[LIS3MDL datasheet]*
    -   *[LIS3MDL app note]*
-   *[evalLSM303D]* **[2]** - Magnetic sensor
-   *[pythonLSM303D]* **[1]** - Magnetic sensor
    -   *[LSM303D datasheet]*
  
##### Voltage buffer with current driver
-   *[evalLT3080]* **[3]** - Current source 0 to 1.1 A TO220
    -   *[LT3080 datasheet]*

##### DAC
-   *[evalDAC80004]* **[2]** - DAC 16 bits with 4 channels
    -   *[DAC80004 datasheet]*

##### H Bridge   
-   *[DRV8838DSGR]* **[10]** - full bridge 0 to 11V
-   *[evalDRV8838DSGR]* **[3]** - full bridge 0 to 11V
    -   *[DRV8838DSGR datasheet]*
    -   *[evalDRV8838DSGR userguide]*

-   *[CPC1002N (SMD)]* **[20]** - Solid state relay - 700 mA, 550 m$\Omega$
    -   *[CPC1002N datasheet]*
       
##### Conectors and wires
-   *[Board connector 5 pins]* **[20]** - Board male connector for wires with locking mechanism
-   *[Wire connector 5 pins]* **[20]** - Wire female connector for the wires
   
-   *[Board connector 6 pins]* **[10]** - Board male connector for wires with locking mechanism
-   *[Wire connector 6 pins]* **[20]** - Wire female connector for the wires

-   *[Wire crimped]* **[50]** - Jumper wires with the crimps already
    -   *[DF13 series documentation]*
-   *[MCU header female 15 pins]* **[10]** - it's the headers to connect the MCU board to the main board

##### Other material
-   *[Resistor]* **[10]** - 6 $\Omega$ resistor 1% 10W
    -   *[Resistor datasheet]*
-   *[micro USB cabe Molex]* **[1]** - Micro USB cable
-   *[micro USB cabe GC]* **[1]** - Micro USB cable **(better)**
-   *[Solderless Protoboard 1]* **[2]** - Protoboard PTH

---

\* **[Quantity]**\
*\* Try to buy everything on **digikey** and **RS-components***

#### Cost: [Cost sheet] [Spread Sheet]

[//]: # "The spread sheet with the price of the components"

[Cost sheet]:https://docs.google.com/spreadsheets/d/e/2PACX-1vSVM6QR7Y6jpUYMwQONXMkUKiQGX6Jbu_LxLJTqZ6yYjJDrseRLFnzkUWpOB_rNdTE3dueEOECVWo1s/pubhtml

[Spread Sheet]:https://docs.google.com/spreadsheets/d/1DiSX0aW9OVdkjEtcynpfPJJRaizZsO2k0Ym7HD6ob9c/edit#gid=0

[//]: # "Magnetic Sensor"

[BM1422AGMV-ZE2]:https://www.digikey.at/product-detail/en/rohm-semiconductor/BM1422AGMV-ZE2/BM1422AGMV-ZE2CT-ND/8620091

[MMC3416 datasheet]:http://www.memsic.com/userfiles/files/Datasheets/Magnetic-Sensors-Datasheets/MMC3416xPJ_Rev_C_2013_10_30.pdf

[evalMMC3416]:https://www.digikey.at/product-detail/en/memsic-inc/MMC34160PJ-B/1267-1044-ND/5658592?cur=EUR&lang=en

[MMC3416]:https://www.digikey.at/product-detail/en/memsic-inc/MMC34160PJ/1267-1062-1-ND/5658606

[//]: # "H bridge - SolidState Relays"

[PVDZ172NPbF (PTH)]:https://www.digikey.at/products/en?keywords=PVDZ172NPbF
[PVDZ172NSPbF (SMD)]:https://www.digikey.at/products/en?keywords=PVDZ172NSPbF
[PVDZ172NPbF datasheet]:https://www.infineon.com/dgdl/pvdz172.pdf?fileId=5546d462533600a401535683ba592934

[CPC1002N (SMD)]:https://www.digikey.at/product-detail/en/ixys-integrated-circuits-division/CPC1002NTR/CLA230CT-ND/1212841
[CPC1002N datasheet]:http://www.ixysic.com/home/pdfs.nsf/www/CPC1002N.pdf/$file/CPC1002N.pdf

[Relay TX-S]:https://www.digikey.at/products/en?keywords=255-3945-5-ND
[TX-S datasheet]:https://www.panasonic-electric-works.com/pew/eu/downloads/ds_61022_en_txs.pdf

[//]: # "H bridge - DRV8838DSGR"

[Digikey Search]:https://www.digikey.at/products/en/integrated-circuits-ics/pmic-full-half-bridge-drivers/746?k=full+h+bridge&k=&pkeyword=full+h+bridge&sv=0&pv1989=0&pv1872=2&pv1872=3&pv1872=4&pv772=543&sf=1&FV=ffe002ea&quantity=&ColumnSort=0&page=1&pageSize=25

[DRV8838DSGR datasheet]:http://www.ti.com/lit/ds/symlink/drv8838.pdf

[evalDRV8838DSGR userguide]:http://www.ti.com/lit/ug/slvua43/slvua43.pdf

[evalDRV8838DSGR]:https://www.digikey.at/products/en/development-boards-kits-programmers/evaluation-and-demonstration-boards-and-kits/787?k=DRV8838

[DRV8838DSGR]:https://www.digikey.at/product-detail/en/texas-instruments/DRV8838DSGR/296-40081-1-ND/5177958

[//]: # "Conectors and wires - Hirose Electric Co Ltd (Seems to be a really good company)"

[Board connector 5 pins]:https://www.digikey.at/product-detail/en/hirose-electric-co-ltd/DF13C-5P-1.25V-50/H3435-ND/530732

[Wire connector 5 pins]:https://www.digikey.at/product-detail/en/hirose-electric-co-ltd/DF13-5S-1.25C/H2182-ND/241752

[Wire connector 6 pins]:https://www.digikey.at/product-detail/en/hirose-electric-co-ltd/DF13-6S-1.25C/H2183-ND/241753

[Board connector 6 pins]:https://www.digikey.at/product-detail/en/hirose-electric-co-ltd/DF13B-6P-1.25V-51/H125996CT-ND/9489658

[Wire crimped]:https://www.digikey.at/products/en/cable-assemblies/jumper-wires-pre-crimped-leads/453?k=Hirose+Electric+Co+Ltd+DF13+wire&k=&pkeyword=Hirose+Electric+Co+Ltd+DF13+wire&sv=0&pv317=1&sf=0&FV=ffe001c5%2C780001%2C13406fe%2C1340700%2C134098f&quantity=&ColumnSort=0&page=1&stock=1&pageSize=25

[DF13 series documentation]:https://media.digikey.com/pdf/Data%20Sheets/Hirose%20PDFs/DF13_Rev2018.pdf

[//]: # "Power Supply and Insulated Copper Wires"

[DP-831A]:https://www.rigol.eu/products/dc-power-loads/dp800/

[PowerSupply Datasheet]:http://beyondmeasure.rigoltech.com/acton/attachment/1579/f-01c1/1/-/-/-/-/DP800%20Datasheet.pdf

[PowerSupply Programming Guide]:https://www.batronix.com/pdf/Rigol/ProgrammingGuide/DP800_ProgrammingGuide_EN.pdf

[RIGOL support]:http://int.rigol.com/Product/Model/46/51

[AWG 23]:https://at.rs-online.com/web/p/kupferdrahte/0357750/

[AWG23 doc]:https://docs-emea.rs-online.com/webdocs/157f/0900766b8157f396.pdf

[AWG 22]:https://at.rs-online.com/web/p/kupferdrahte/7790729/

[//]: # "The micro-controllers"

[STM32L432KCU6]:https://at.rs-online.com/web/p/products/1438574/?grossPrice=Y&cm_mmc=AT-PLA-DS3A-_-google-_-CSS_AT_DE_Halbleiter_Whoop-_-(AT:Whoop!)+Entwicklungskits+Prozessor+%26+Mikrocontroller-_-PRODUCT_GROUP&matchtype=&pla-300344841813&gclid=Cj0KCQiAtbnjBRDBARIsAO3zDl9tvOzd_QteO2xSP4sqNIqKobPY6synfCSenqFWTy26DS_MTh0n_o0aAs1FEALw_wcB&gclsrc=aw.ds

[MCU header female 15 pins]:https://www.digikey.at/product-detail/en/sullins-connector-solutions/PPPC151LFBN-RC/S7048-ND/810187

[STM32L4 datasheet]:https://www.st.com/resource/en/datasheet/stm32l432kc.pdf

[STM32L4 doc]:https://www.st.com/content/st_com/en/products/microcontrollers-microprocessors/stm32-32-bit-arm-cortex-mcus/stm32-ultra-low-power-mcus/stm32l4-series/stm32l4x2/stm32l432kc.html#design-scroll

[//]: # "Others"

[BluetoothModule]:https://www.banggood.com/de/HC-05-Wireless-Bluetooth-Serial-Transceiver-Module-Slave-And-Master-p-908621.html?gmcCountry=AT&currency=EUR&createTmp=1&utm_source=googleshopping&utm_medium=cpc_bgs&utm_content=xibei&utm_campaign=pla-at-ele-diy-pc&gclid=Cj0KCQiAtbnjBRDBARIsAO3zDl-b7ZuU5DxXRajhRKpf8Khox6KHiB1R3YNv15VnllpM98te19_KQiYaAqYgEALw_wcB&cur_warehouse=CN

[coolBluetoothModule]:https://at.rs-online.com/web/p/bluetooth-module/1368063/

[micro USB cabe Molex]:https://www.digikey.at/product-detail/en/molex/0687840003/WM17147-ND/1952432

[micro USB cabe GC]:https://www.digikey.at/product-detail/en/gc-electronics/45-1430-3/GC14303-ND/2529126

[Solderless Protoboard 1]:https://www.digikey.at/product-detail/en/mikroelektronika/MIKROE-1097/1471-1010-ND/4495375

[Solderless Protoboard 2]:https://www.digikey.at/product-detail/en/twin-industries/TW-E41-102B/438-1047-ND/643113

[//]: # "BackUp - Things that I will probably not use anymore, but can be usefull in the future"

[//]: # "Raw components for the PCB's"

[DAC80004]:https://www.digikey.at/product-detail/en/texas-instruments/DAC80004IPW/296-44598-5-ND/6126022

[LT3085]:https://www.digikey.at/product-detail/en/linear-technology-analog-devices/LT3085EMS8E-PBF/LT3085EMS8E-PBF-ND/1952899

[LT3080]:https://at.rs-online.com/web/p/ldo-spannungsregler/1646075/

[LIS3MDL]:https://www.digikey.at/product-detail/en/stmicroelectronics/LIS3MDLTR/497-13892-1-ND/4309737

[Resistor]:https://www.digikey.at/product-detail/en/vishay-dale/MRA-126R000FE12/MRA12-6.0-ND/953781

[//]: # "The evaluation boards"

[evalDAC80004]:https://www.digikey.at/product-detail/en/texas-instruments/DAC80004EVM/296-44555-ND/6128437

[evalLIS3MDL]:https://www.digikey.at/product-detail/en/stmicroelectronics/STEVAL-MKI137V1/497-14106-ND/4280206

[evalLT3080]:https://www.digikey.at/products/en?keywords=DC995A

[evalLSM303D]:https://www.digikey.at/product-detail/en/pimoroni-ltd/PIM376/1778-1237-ND/9607918

[pythonLSM303D]:https://www.digikey.at/product-detail/en/pimoroni-ltd/PIM027/1778-1027-ND/6928240

[//]: # "Würth elektronik (Not the best for connectors)"

[SMD male WTB connector 4]:https://www.digikey.at/product-detail/en/wurth-electronics-inc/653104124022/732-2725-1-ND/2508674

[SMD male WTB connector 5]:https://www.digikey.at/product-detail/en/wurth-electronics-inc/653105124022/732-2726-1-ND/2508675

[Female WTB connector 4]:https://www.digikey.at/product-detail/en/wurth-electronics-inc/653004113322/732-2884-ND/2508653

[Female WTB connector 5]:https://www.digikey.at/product-detail/en/wurth-electronics-inc/653005113322/732-2885-ND/2508654

[//]: # "Datasheets and aplication notes"

[LSM303D datasheet]:https://www.pololu.com/file/0J703/LSM303D.pdf

[LIS3MDL datasheet]:https://www.st.com/resource/en/datasheet/lis3mdl.pdf

[LIS3MDL app note]:https://www.pololu.com/file/0J1090/LIS3MDL-AN4602.pdf

[LT3080 datasheet]:https://www.analog.com/media/en/technical-documentation/data-sheets/3080fc.pdf

[LT3085 datasheet]:https://www.analog.com/media/en/technical-documentation/data-sheets/3085fb.pdf

[DAC80004 datasheet]:http://www.ti.com/lit/ds/symlink/dac60004.pdf

[Resistor datasheet]:http://www.vishay.com/docs/31801/mra.pdf

[AWG22 doc]:https://docs-emea.rs-online.com/webdocs/1218/0900766b812189ac.pdf

---

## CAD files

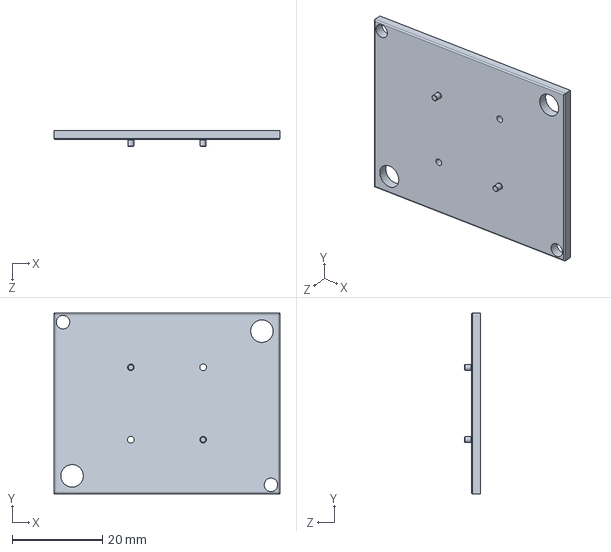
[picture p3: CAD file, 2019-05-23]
3DModelFiles/sampleSupport.SLDPRT
50.0 x 40.0 x 3.50 mm

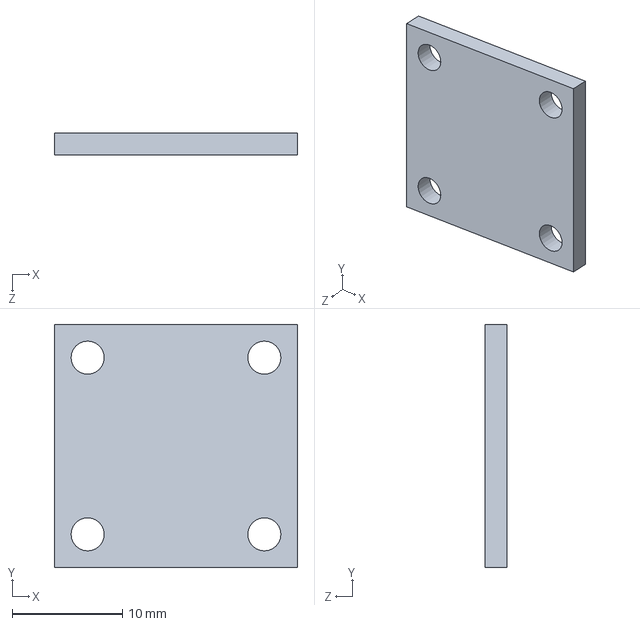
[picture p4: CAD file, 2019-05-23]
3DModelFiles/sample.SLDPRT
22.0 x 22.0 x 2.00 mm

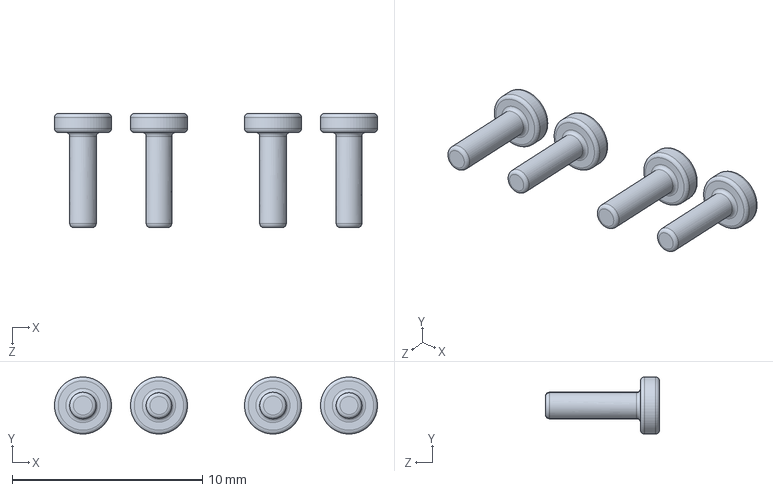
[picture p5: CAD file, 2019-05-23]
3DModelFiles/pegs1-5mm.SLDPRT
17.0 x 3.00 x 6.00 mm

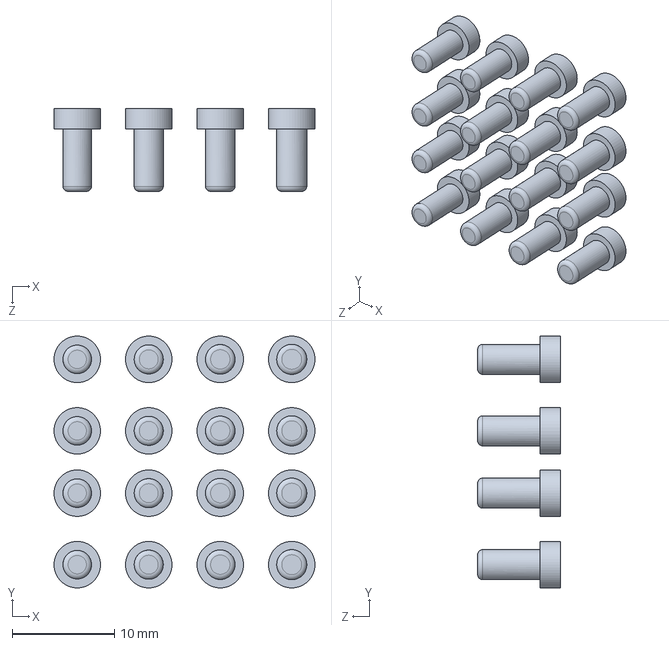
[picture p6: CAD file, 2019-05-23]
3DModelFiles/pegs3mm.SLDPRT
25.6 x 24.6 x 8.10 mm

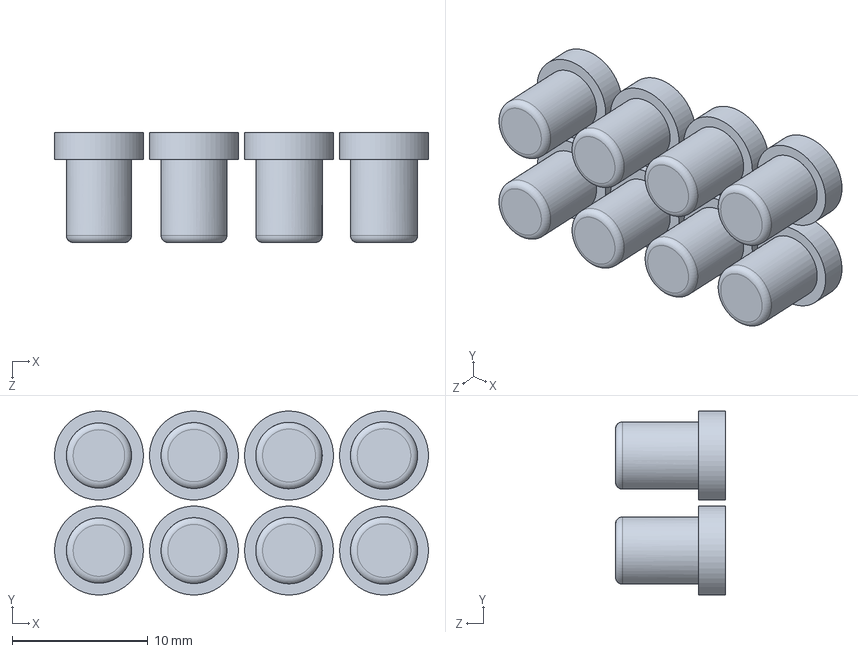
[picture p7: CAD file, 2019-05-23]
3DModelFiles/pegs5mm.SLDPRT
27.6 x 13.5 x 8.10 mm

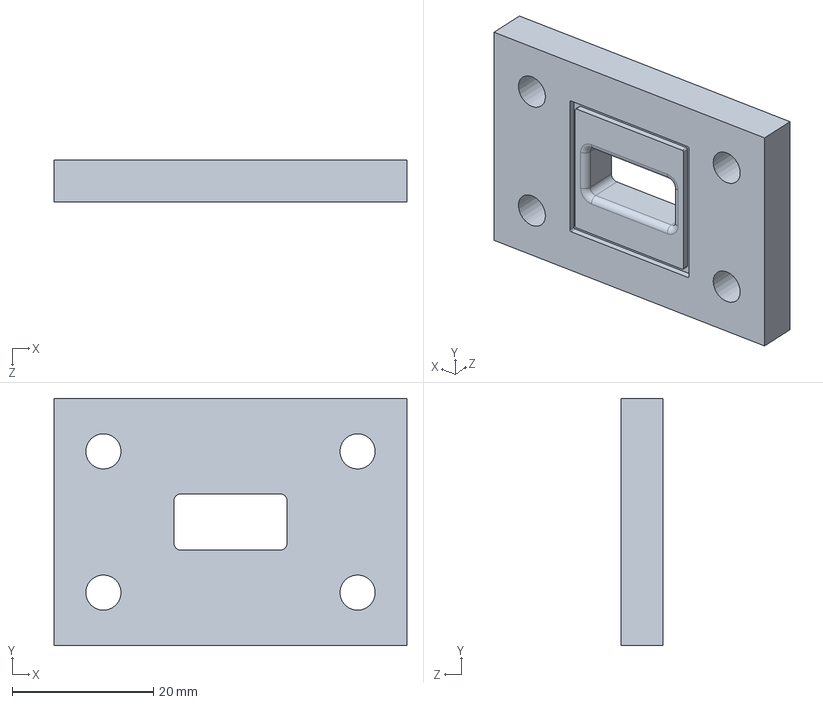
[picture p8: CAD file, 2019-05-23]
3DModelFiles/samplesBase.SLDPRT
50.0 x 35.0 x 6.00 mm

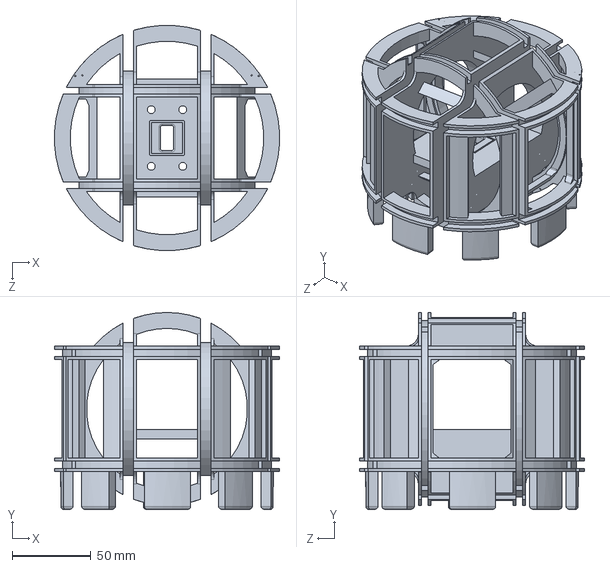
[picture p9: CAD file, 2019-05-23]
3DModelFiles/3DHC.SLDPRT
143.1 x 125.3 x 143.3 mm

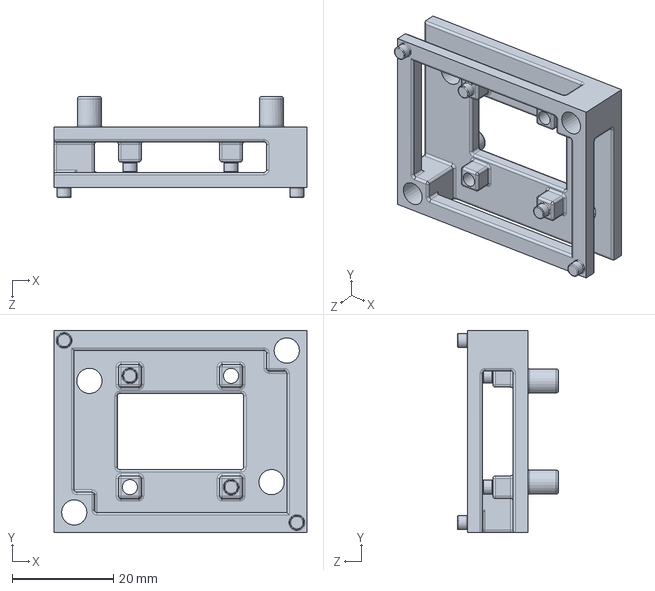
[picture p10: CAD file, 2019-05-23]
3DModelFiles/supportForTheSensorAndSampleSupport.SLDPRT
50.0 x 40.0 x 20.0 mm

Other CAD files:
3DModelFiles/3DHC.STL
3DModelFiles/pegs1-5mm.STL
3DModelFiles/pegs3mm.STL
3DModelFiles/pegs5mm.STL
3DModelFiles/sample.STL
3DModelFiles/sampleSupport.STL
3DModelFiles/samplesBase.STL
3DModelFiles/supportForTheSensorAndSampleSupport.STL

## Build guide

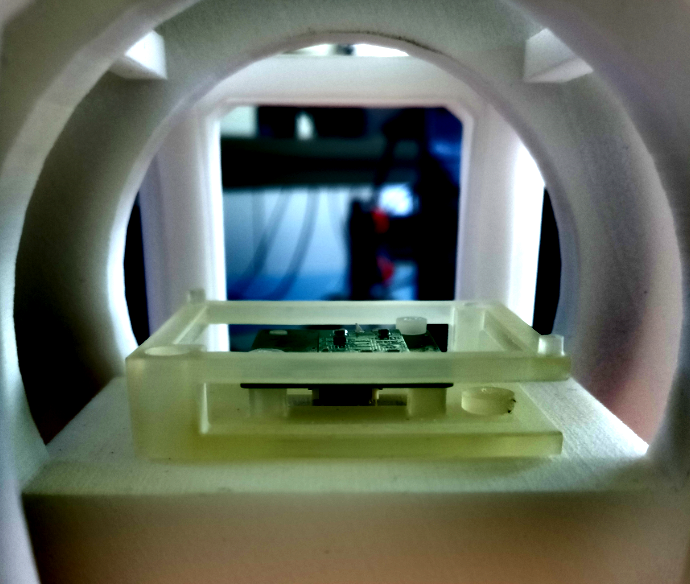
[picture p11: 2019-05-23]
Images/Print results/asw2f.png

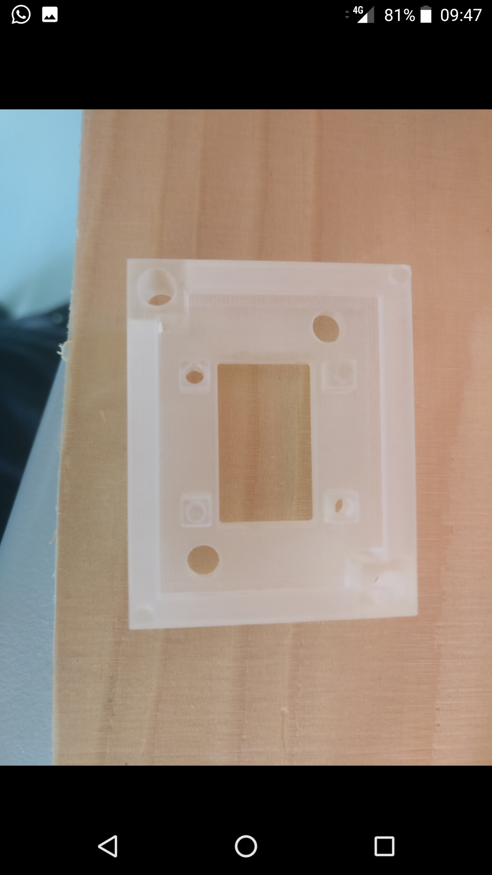
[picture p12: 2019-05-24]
Images/Print results/Screenshot_20190524-094706.jpg

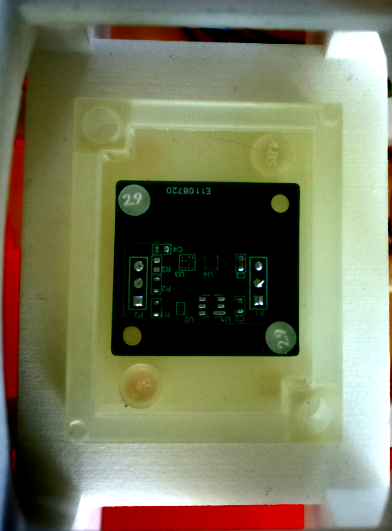
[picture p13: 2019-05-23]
Images/Print results/sd245tf.png

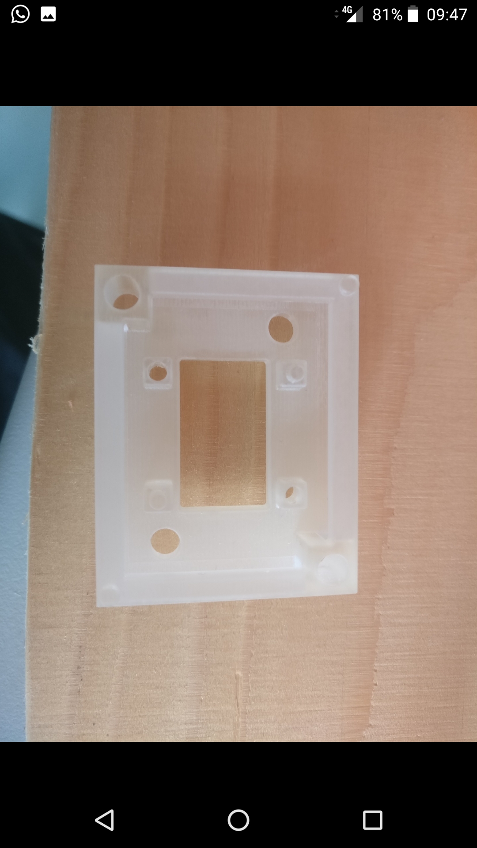
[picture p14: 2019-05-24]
Images/Print results/Screenshot_20190524-094711.jpg

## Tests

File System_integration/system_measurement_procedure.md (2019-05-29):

```python
 # -*- coding: utf-8 -*-
"""
Created on Mon May 13 13:02:43 2019

@author: CTR Magnetic Demo
"""

#%% Imports

import numpy as np
import csv
from time import sleep
from auxLib import  updateCoilPolarity, getDataFromReader, rotationMatrixCalculator, strToFloat, storeDataObj, writeDataOnFile, CurrentCalculatorObj, setField, startupCoilsPolarity, closeFile, closeSerialObj, createAndOpenFile, WhatTimeIsIt, makeDir, createSerialObj, COMdetect, changeCoilPolarity, measurementNtransformation, setPowerSupplyChVoltage, setPowerSupplyAllChVoltage, setPowerSupplyAllChCurrent, setupMCU, closingPowerSupplyChannel, startUpPowerSupply, getMeasurement, setPowerSupplyChCurrent

#%% User code

samplesPerMean = b'2'
timeBetweenSamples = b'100'
measurementPeriod = 0.00

csvPath = "./csvData/"
csvFileName = "fieldsNcurrents2"

#%%

# To show numbers in console in the raw representation
np.set_printoptions(suppress=True)

fileField = csvPath + csvFileName + ".csv"

file = open(fileField, 'r')
reader = csv.reader(file, delimiter=';', quoting=csv.QUOTE_NONE)
floatData, channel, zeroField, rotationMatrixMeasures, control = getDataFromReader(reader, 1)
file.close()

#%% Start up code    
#closeSerialObj(serialObj)
# Teorethical values for field/current ration
teorethicalRelationship = [0.5, 2.5, 0.5]

try:
    # opening MCU comunication
    COM = COMdetect()
    
    serialObj = createSerialObj(COM)
        
    # Opening the MCU comunication channel
    setupMCU(serialObj, samplesPerMean, timeBetweenSamples)
    sleep(0.1)
    startupCoilsPolarity(serialObj)
    
    resource_name = 'USB0::0x1AB1::0x0E11::DP8A203800261::0::INSTR'       
    rm, dp800 = startUpPowerSupply(resource_name)
    
    rotationMatrix = rotationMatrixMeasures
       
    # comparing the zero fields
    setPowerSupplyAllChVoltage(dp800, 4)
    setPowerSupplyAllChCurrent(dp800, 0)
    
    fData = getMeasurement(serialObj)
    zeroFieldMeasured = np.matmul(rotationMatrix, fData)
    
    error = np.zeros((3,1))
    for i in range(0,3):
        error [i]= (zeroFieldMeasured[i] - zeroField[i])
    print("zero field absolute diference:")
    print(error)
    
    currentOffset = [0,0,0]
    
    for i in range(0,3):
        currentOffset[i] = 0#error[i]/teorethicalRelationship[i]    
            
    currents = floatData[3]
    newMeasures = np.zeros((len(currents),3))
    errors= np.zeros((len(currents),3))
    dp800.write("DISP:MODE NORM")
    sleep(0.01)
    i = 0
    indexSum = 1
    while(1):
        #print(currents[i])
        #print(channel[i])
        xablau = (currents[i]-currentOffset[channel[i]-1])
        updateCoilPolarity(serialObj, xablau, channel[i])
        dp800.write('SOUR'+str(int(channel[i]))+':CURR '+str(float(xablau/1000)))
        sleep(0.01)
        i += indexSum
        if i == 3:
            indexSum = 1
        if i == len(currents):
            i = 3
    
    while(1):
            
        if str(control[i]) == "['Current']":
            xablau = (currents[i]-currentOffset[channel[i]-1])
            updateCoilPolarity(serialObj, xablau, channel[i])
            setPowerSupplyChCurrent(dp800, channel[i], float(xablau/1000))
            setPowerSupplyChVoltage(dp800, channel[i], 4)
        else:
            updateCoilPolarity(serialObj, currents[i], channel[i])
            setPowerSupplyChVoltage(dp800, channel[i], float(currents[i]/1000))
            setPowerSupplyChCurrent(dp800, channel[i], 0.5)
            
        sleep(measurementPeriod)
            
        fData = getMeasurement(serialObj)
        fData = np.matmul(rotationMatrix, fData)
        nsei = 3
        for j in range(0,3):
            newMeasures[i][j] = fData[j]
            errors[i][j] = newMeasures[i][j] - floatData[j][i]
        i += indexSum
        if i == 4:
            indexSum = 1
        if i == len(currents):
            i = 4
    
    print('absolute diference between measured field and expected field:')
    print(errors)
    print('absolute measured field:')
    print(newMeasures)
    
    closeSerialObj(serialObj)
    closingPowerSupplyChannel(dp800, rm)
    
except Exception as error:

    print(error)
    
    closeSerialObj(serialObj)
    closingPowerSupplyChannel(dp800, rm)

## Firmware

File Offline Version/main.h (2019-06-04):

/**
  ******************************************************************************
  * @file           : main.h
  * @brief          : Header for main.c file.
  *                   This file contains the common defines of the application.
  ******************************************************************************
  * @attention
  *
  * <h2><center>&copy; Copyright (c) 2019 STMicroelectronics.
  * All rights reserved.</center></h2>
  *
  * This software component is licensed by ST under BSD 3-Clause license,
  * the "License"; You may not use this file except in compliance with the
  * License. You may obtain a copy of the License at:
  *                        opensource.org/licenses/BSD-3-Clause
  *
  ******************************************************************************
  */

/* Define to prevent recursive inclusion -------------------------------------*/
#ifndef __MAIN_H
#define __MAIN_H

#ifdef __cplusplus
extern "C" {
#endif

/* Includes ------------------------------------------------------------------*/

#include <stdio.h>
#include <stdlib.h>
#include <string.h>
#include "stm32l4xx_it.h"
#include "lib_aux.h"
#include "MCC3416_def.h"
#include "stm32l4xx_hal.h"

/* Exported functions prototypes ---------------------------------------------*/
void Error_Handler(void);

/* Private defines -----------------------------------------------------------*/
#define MCO_Pin GPIO_PIN_0
#define MCO_GPIO_Port GPIOA
#define VCP_TX_Pin GPIO_PIN_2
#define VCP_TX_GPIO_Port GPIOA
#define DATAREADY_Pin GPIO_PIN_8
#define DATAREADY_GPIO_Port GPIOA
#define DATAREADY_EXTI_IRQn EXTI9_5_IRQn
#define SWDIO_Pin GPIO_PIN_13
#define SWDIO_GPIO_Port GPIOA
#define SWCLK_Pin GPIO_PIN_14
#define SWCLK_GPIO_Port GPIOA
#define VCP_RX_Pin GPIO_PIN_15
#define VCP_RX_GPIO_Port GPIOA
#define LD3_Pin GPIO_PIN_3
#define LD3_GPIO_Port GPIOB

#define PHEx_Pin GPIO_PIN_4
#define PHEx_GPIO_Port GPIOB
#define PHIn_Pin GPIO_PIN_5
#define PHIn_GPIO_Port GPIOB
#define SSRPA_Pin GPIO_PIN_0
#define SSRPA_GPIO_Port GPIOB
#define SSRPB_Pin GPIO_PIN_7
#define SSRPB_GPIO_Port GPIOB
#define SSRNA_Pin GPIO_PIN_6
#define SSRNA_GPIO_Port GPIOB
#define SSRNB_Pin GPIO_PIN_1
#define SSRNB_GPIO_Port GPIOB

#define TRUE 	1
#define FALSE 	0

#ifdef __cplusplus
}
#endif

#endif /* __MAIN_H */

/************************ (C) COPYRIGHT STMicroelectronics *****END OF FILE****/

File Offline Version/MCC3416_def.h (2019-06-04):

/* Define to prevent recursive inclusion -------------------------------------*/
#ifndef __MMC3416_DEF_H
#define __MMC3416_DEF_H

#ifdef __cplusplus
extern "C" {
#endif

// MMC3416 I2C slave address, the 3 LSB can change with the order code, (example) order code = 4, so the 3 LSB will be 010
#define MMC3416_SLAVE_ADDR				  		0x30

// MMC3416 registers address
typedef enum MMC_regs {
	MMC3416REG_X_L = 0,
	MMC3416REG_X_H,
	MMC3416REG_Y_L,
	MMC3416REG_Y_H,
	MMC3416REG_Z_L,
	MMC3416REG_Z_H,
	MMC3416REG_STATUS,
	MMC3416REG_CTRL0,
	MMC3416REG_CTRL1,
	MMC3416REG_PRODUCTID = 0x20
}MMC_REGS;



// Convert the 16 bits two's complement representation to uT
// Value uT = raw16BitsValue*100/MMC3416_Scale_Adjust;

#define MMC3416_Scale_Adjust_12Bits 	    	128
#define MMC3416_Scale_Adjust_14Bits 		  	512
#define MMC3416_Scale_Adjust_16Bits				2048

#ifdef __cplusplus
}
#endif

#endif /* __MMC3416_DEF_H */

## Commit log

2019-05-23 printed parts
2019-05-28 vai que
